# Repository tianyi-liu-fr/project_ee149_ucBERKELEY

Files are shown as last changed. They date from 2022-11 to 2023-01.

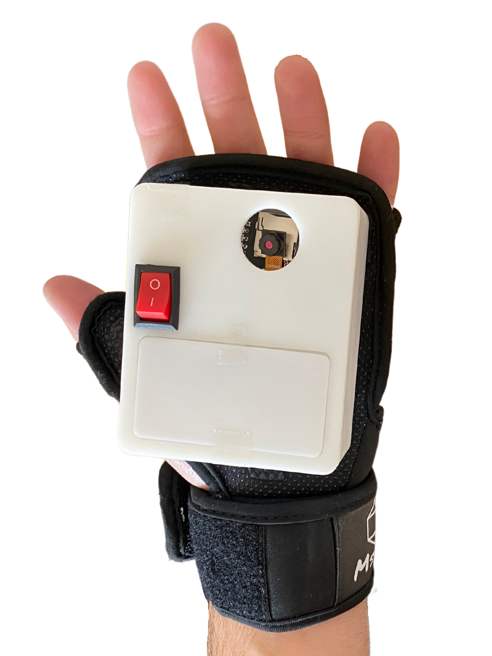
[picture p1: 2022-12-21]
Hardware/Device (front view).png

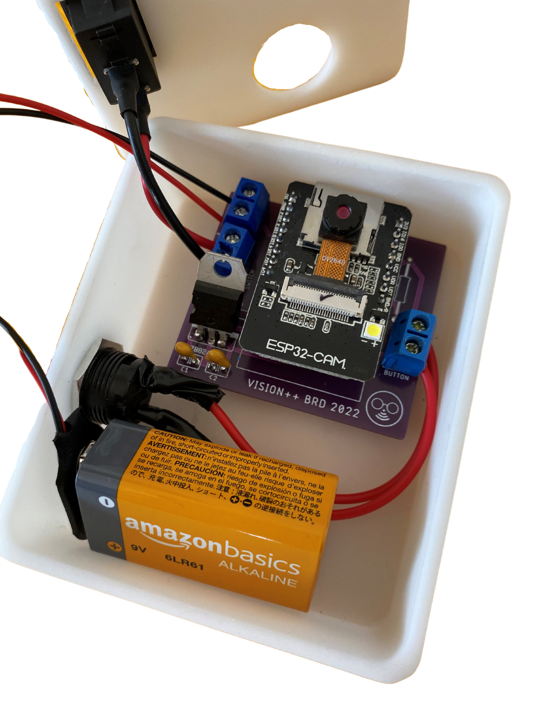
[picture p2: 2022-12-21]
Hardware/Open enclosure.png

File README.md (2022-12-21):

# EECS149/249 VISION++ Project
Project developed by Enrique Flores Medina and Tianyi Liu, as conceptualized by PhD Prabal Dutta.


Device and app

Vision++ is a glove designed to empower low vision people, by turning any readable text into speech. By pressing a button, the glove captures an image. If it contains any text, it is automatically turned into speech through a smartphone app. Demonstration video: https://youtu.be/q09WU-yeQec

# Hardware
The hardware folder contains the files used to design a PCB and an enclosure. The ESP32-CAM development board was used, and a PCB and enclosure were designed to adjust to its capabilities.

# Software
The software folder contains the source code for the ESP32-CAM, which allows it to capture and upload images to a cloud server with the press of a button. It also contains two python scripts: one downloads the images uploaded by the ESP32-CAM to the cloud server, and another one extracts the text detected in those images. Finally, the Smartphone App folder contains the file used to develop the app that turns the text into speech. Additionally, there is a Finite State Machine (FSM) diagram showing the behavior of each piece of software.

# Documentation
The documentation folder includes the project proposal and two milestones, showing how the project started, how it progressed, and how it turned out in the end.

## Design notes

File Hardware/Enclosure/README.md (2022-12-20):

# Enclosure CAD
Consists of 3 separate parts: A base, which contains the PCB, the battery, the power switch, and the button. A base cover, sealing everything inside the enclosure. A battery cover, which allows for battery replacement.

For the project, the enclosure was 3D printed with LEDO 6060 Resin, and the electronic components were attached to the enclosure with polymer glue.

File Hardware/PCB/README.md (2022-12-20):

# What is in the PCB?
The PCB allows for the connection of pin 13 in the ESP32-CAM board to GND through a push button, which serves as the trigger to capture images. It also allows for the use of power supplies from 5VDC up to 35VDC, by using an L7805 5V voltage regulator and two capacitors for noise filtering. Finally, the PCB is equipped with a voltage divisor that is connected to an ADC pin in the board. If a 9VDC battery is used as the power supply, two 10kOhm resistors can be used to measure its voltage level. This last part, however, is not yet implemented in the source code. 

The images show a CAD of the PCB and of the real assembled PCB. The real assembled PCB shown in outdated.

# Libraries
Footprint for the ESP32-CAM development board as ESP32-CAM.lbr, and footprint for the L7805 voltage regulator as L7805.lbr

# Board, Schematic, and Gerbers
Files for the PCB design are shown as PCB.brd, PCB.sch, and Gerbers.zip. The pinout for the ESP32-CAM development board can be found in: https://randomnerdtutorials.com/esp32-cam-ai-thinker-pinout/

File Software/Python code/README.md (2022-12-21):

# Python code
Two python scripts were used for the project.
1. Download images from Google Drive

This script automatically downloads the images taken by the camera and uploaded to the Google Drive folder. After they are downloaded, the script deletes them from Google Drive, minimizing the storage use of the cloud service.

2. AWS Textract

This script automatically processes the images downloaded to the computer by the previous script with AWS textract. After the text is detected, it is written in a Google Spreadsheet.

Note: Both python scripts are run simultaneously when the device is being used.

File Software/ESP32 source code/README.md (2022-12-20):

# Code to capture and upload images to Google Drive
A template source code to upload images to Google Drive using the ESP32-CAM board, found in the folder ESP32_GoogleDrive, was extracted from https://www.electroniclinic.com/esp32-cam-send-images-to-google-drive-iot-security-camera/. Copyright (c) 2022 Engr Fahad.

Three external libraries are used in the source code:
1. "esp_camera.h", which is the ESP32 camera driver. Copyright (c) 2015-2016 Espressif Systems (Shanghai) PTE LTD. License: https://github.com/espressif/esp32-camera
2. "Base64.h", used to encode binary into base64 strings. Copyright (c) 2013 Adam Rudd. License: https://github.com/adamvr/arduino-base64 
3. "soc.h", used to disable the brownout detector, which creates restrictions due to low power supply. Copyright (c) 2010-2022 SPDX-FileCopyrightText Espressif Systems (Shanghai) CO LTD. License: https://github.com/espressif/esp-idf/blob/master/components/soc/esp32/include/soc/soc.h

Furthermore, Arduino core for ESP32 was installed in the Arduino IDE, from https://github.com/espressif/arduino-esp32. The following URL https://raw.githubusercontent.com/espressif/arduino-esp32/gh-pages/package_esp32_index.json was added as a board manager to do so. Copyright (C) 1991, 1999 Free Software Foundation, Inc.

# Modifications to the original code
The original template source code sends a notification when the image is uploaded using Line Notify. This part was removed, since it was not necessary for the purposes of the project. Comments on the relevance of each line of code were added. The original code sends an image to Google Drive periodically using a delay in the main loop function. A GPIO pin set as an input was added to use a button as the trigger to send images. Furthermore, the number of frames that can be stored in the camera's buffer was reduced from 2 to 1, preventing the uploading of images that were not sent in previous triggerings of the button.

# Google Apps Script
A javascript Google Apps Script, which helps to provide credential authentication and upload images to specific Google Drive folders, was deployed. The deployment ID is used in the source code for the ESP32-CAM board. The template for the Google Apps Script was also extracted from https://www.electroniclinic.com/esp32-cam-send-images-to-google-drive-iot-security-camera/. Copyright (c) 2022 Engr Fahad. The notification with Line Notify was eliminated from the script.

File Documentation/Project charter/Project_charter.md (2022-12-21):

# VISION++
Team: Enrique Flores Medina, Tianyi Liu.

EECS 149/249A Project Charter, Fall, 2022

# Project Goal
This project will develop a glove that enables blind people to read, by turning (almost) any text they
encounter into speech.

# Project Approach
The project will convert any text into speech as described by a deterministic state machine that receives
multiple sensor inputs. One of these inputs will trigger a camera, which will take a picture and send it to a
computer. Then, the computer will read the text in the received image, and convert it into speech that can
be heard with either headphones or a speaker.

# Resources
Our plan is to use a microcontroller (SparkFun ESP32 Thing - DEV-13907) as the main distributor
between the embedded camera and the computer. The picture taken by the embedded camera will be
transferred wirelessly with BLE or WIFI. Then, using MATLAB’s OCR function, the text will be
extracted from the picture. Finally, the text will be turned into speech using MATLAB’s audio toolbox.
With regards to the embedded camera that will be used for the project, the first option would be the
ESP32-CAM WiFi Bluetooth Camera Module Development Board With Camera (D111), since it is the
most hardware friendly for the ESP32 board.

The first goal is the transferring of images from the microcontroller via WIFI/BLE. By pushing a button
(from the hardware inventory), the microcontroller should instruct the camera to take a picture, and send
it. The second goal is to use MATLAB to read and speak out all the text from the picture (from the
hardware inventory). Finally, the third goal would be the addition of an ultrasonic sensor (from the
hardware inventory) to instruct the user on a proper distance to take the picture from, but this is not the
main focus. The state machine would take, then, the ultrasonic sensor measurements and the button as
inputs.

# Schedule
● October 21: Project Proposal (this document) and creation of Github repository

● October 31: Architecture drawing (state machine), finalize the hardware list with GSI approval

● November 6: Milestone 1

● November 14: Reliable MATLAB script to read text from images taken with the embedded
camera and turn it into speech. Add a light source to illuminate the text every time the photo is
taken. Decide on the protocol to send the picture from the ESP32 to the computer.

● November 21: Midterm 2

● November 22: Prepare Milestone 2 and code to send the image from the microcontroller to the
computer.

● November 23: Milestone 2

● November 28 - December 2: Milestone 2 Meetings

● December 7: Finalize details, if there is extra time:
  1. Add ultrasonic sensor measurements to determine how far the user has to be from the text
to take the image properly.
  2. Create an app to hear the speech on the phone

● December 15: Project Poster/Demo Expo

● December 16: Peer Evaluations, Project report

# Risk and Feasibility
There are many unknowns. First, by sending the image from the microcontroller to the computer, some
packets could be lost. Therefore, the image could lose quality which would significantly reduce our ability
to detect the text in it. To deal with this, a comparison between the reliability of the image transmission
between BLE and serial bus could be taken. Another potential issue could be the latency from the trigger
of the camera to the speech, which could make the functionality of the product inefficient. If the system
consumes a lot of power, and the hardware components are not ergonomic for the user, the experience
would also be worsened.

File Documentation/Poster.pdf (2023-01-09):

# EECS 149/249A

Fall 2018 | VISION++

Enrique Flores Medina, Tianyi Liu

## Goals

VISION++ seeks to empower low vision people by providing them a glove that can turn any text into speech.

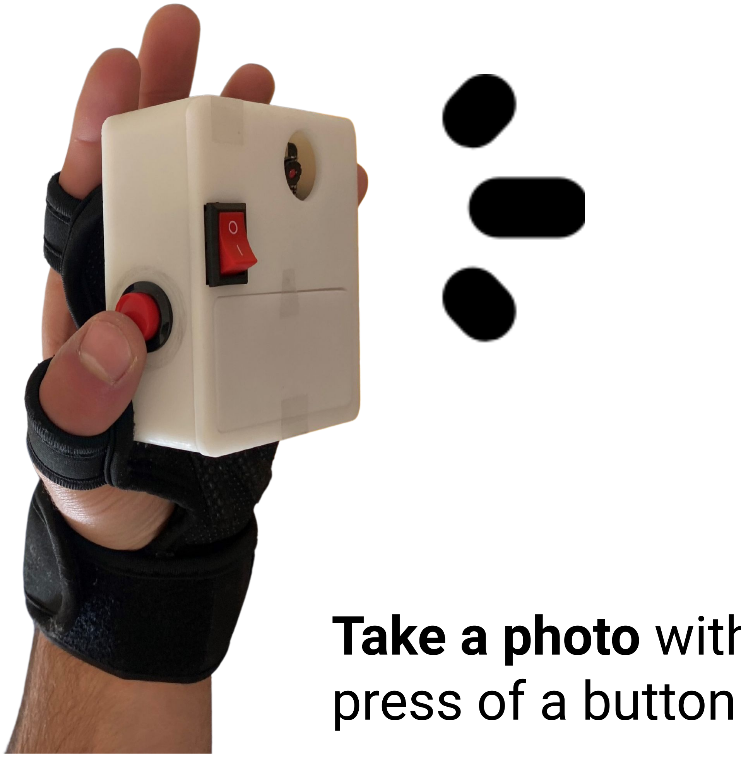
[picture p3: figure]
press of a button
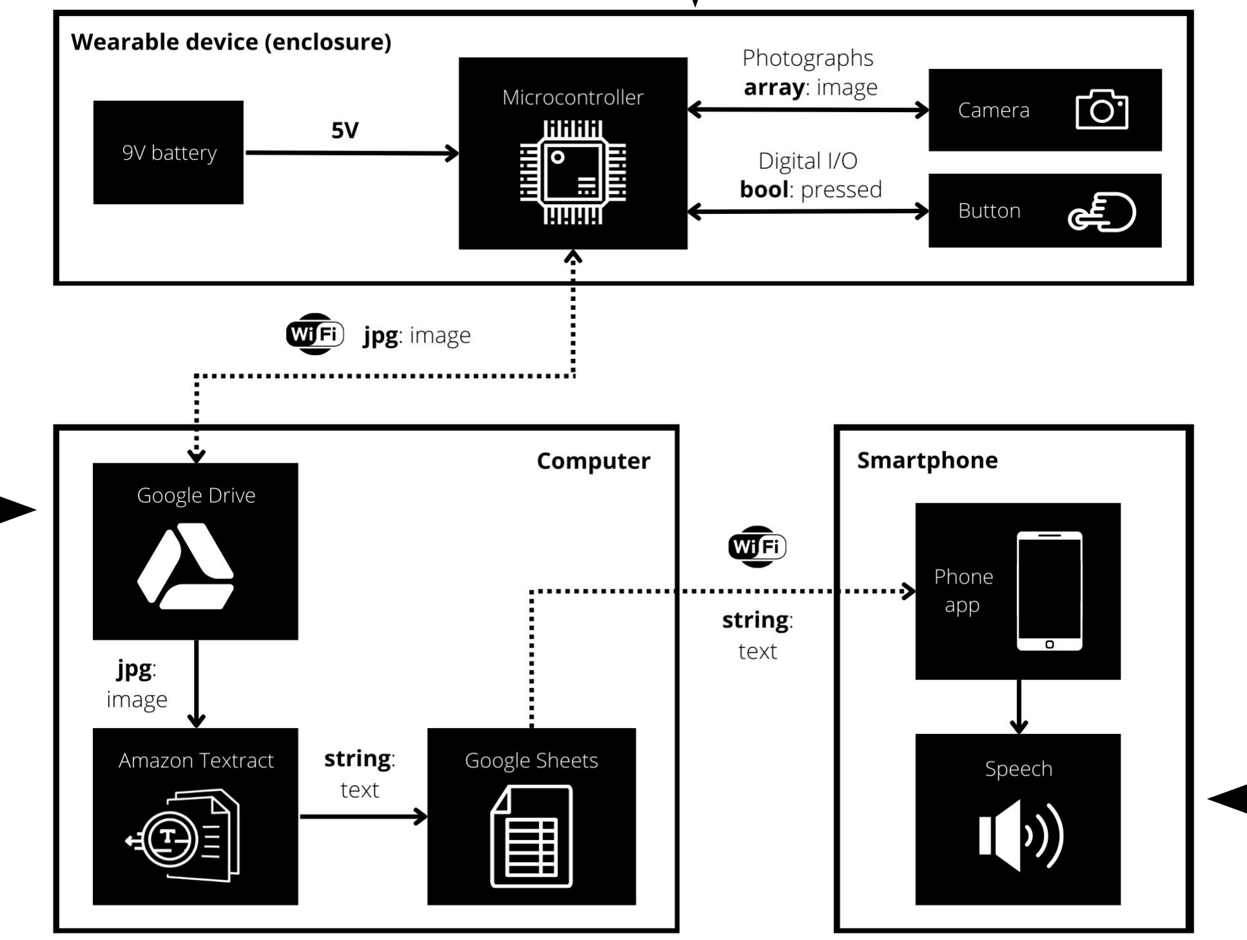
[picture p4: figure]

Take a photo with the

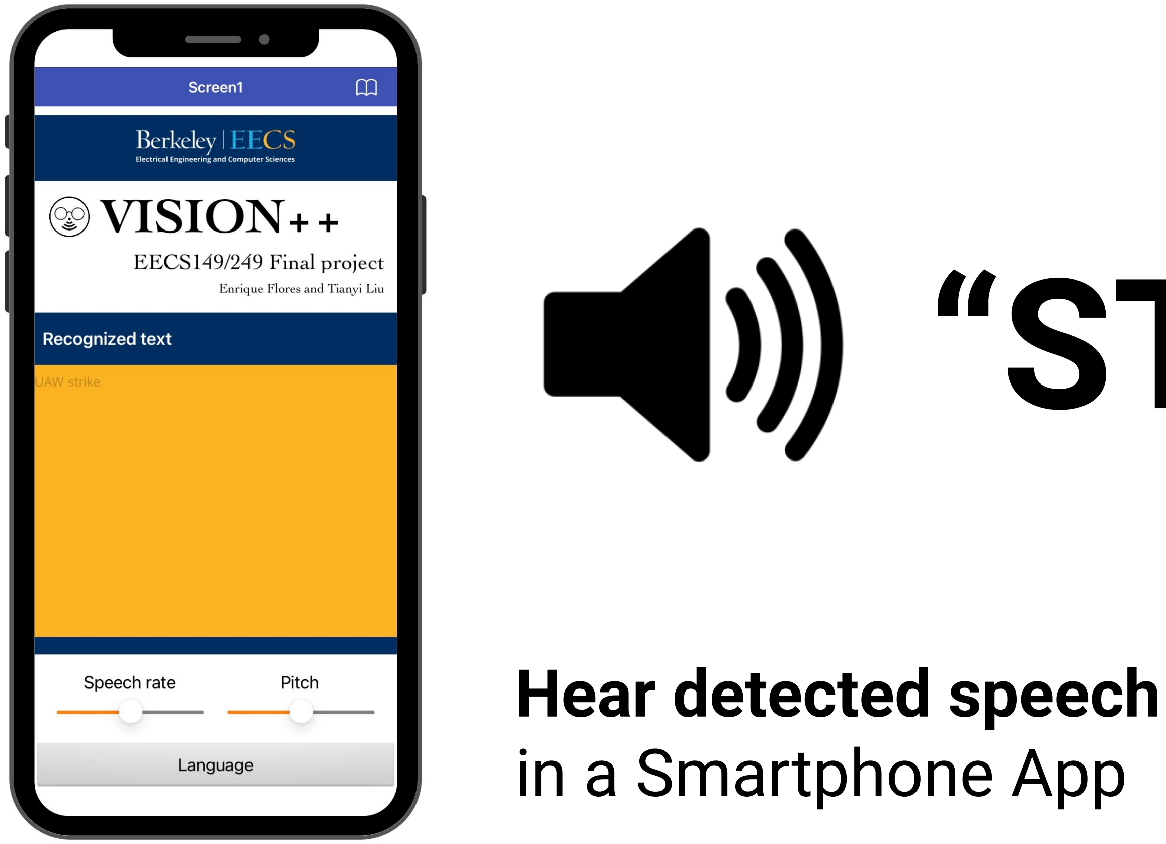
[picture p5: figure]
Hear detected speech in a Smartphone App

The glove includes an
ESP32-CAM development board, which includes a wifi module, an OV2640 camera, an easy to

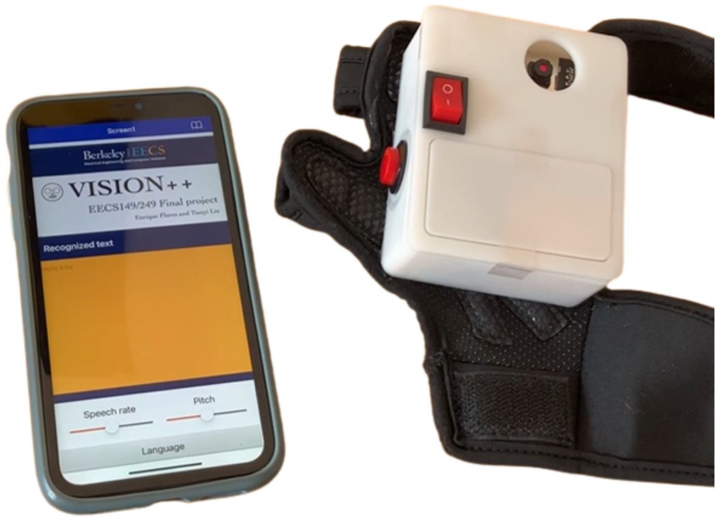
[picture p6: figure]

replace 9V battery, and a button. The app allows the user to select a language, speech rate and pitch.

### 1. Enable your phone’s

hotspot.

### 2. Turn on device and

wait for it to connect
to the network.

### 3. Ready to use!

## Project architecture

The following diagram shows the communication between the different parts that make up the project.

This is in the glove

## Behavior of the system

2022

# “STOP”

## What is in the glove and app?

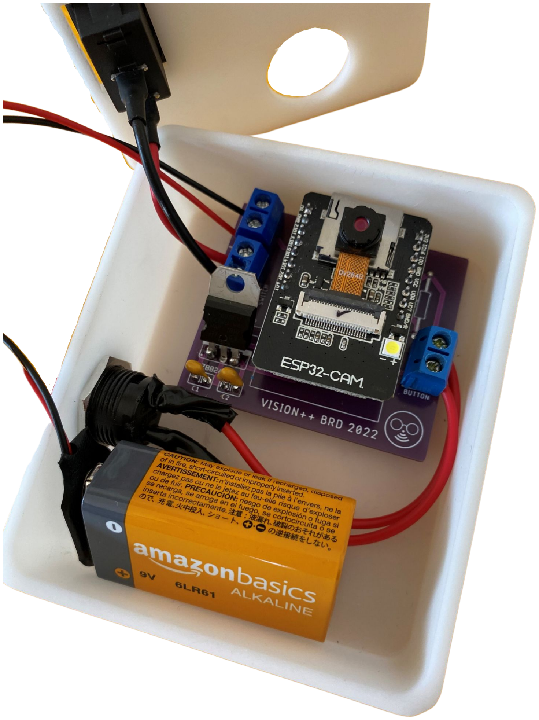
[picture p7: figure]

## How can I use it?

Now, press the button
and hear the speech

A computer

Smartphone

- The glove captures an image and uploads it to Google Drive through WiFi
- A computer downloads it, extracts the text with AWS Textract, and uploads it to a Google Spreadsheet
- The smartphone app turns the text into speech

The following state
machine displays the
behavior of the entire
system.

The only input is the push of the button, and the speaker

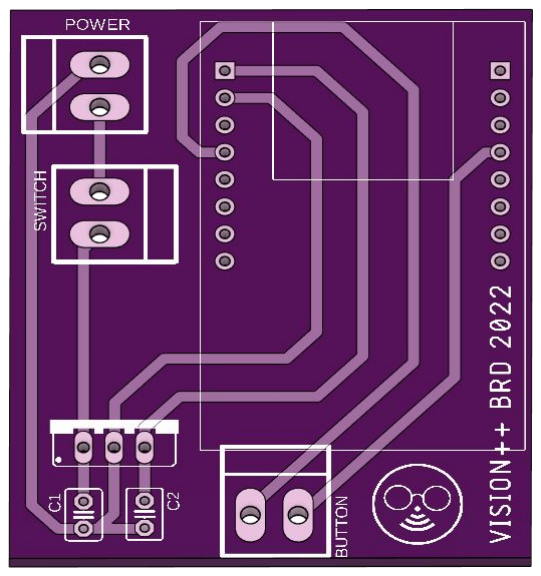
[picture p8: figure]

of the phone and the
camera of the glove are
treated as outputs

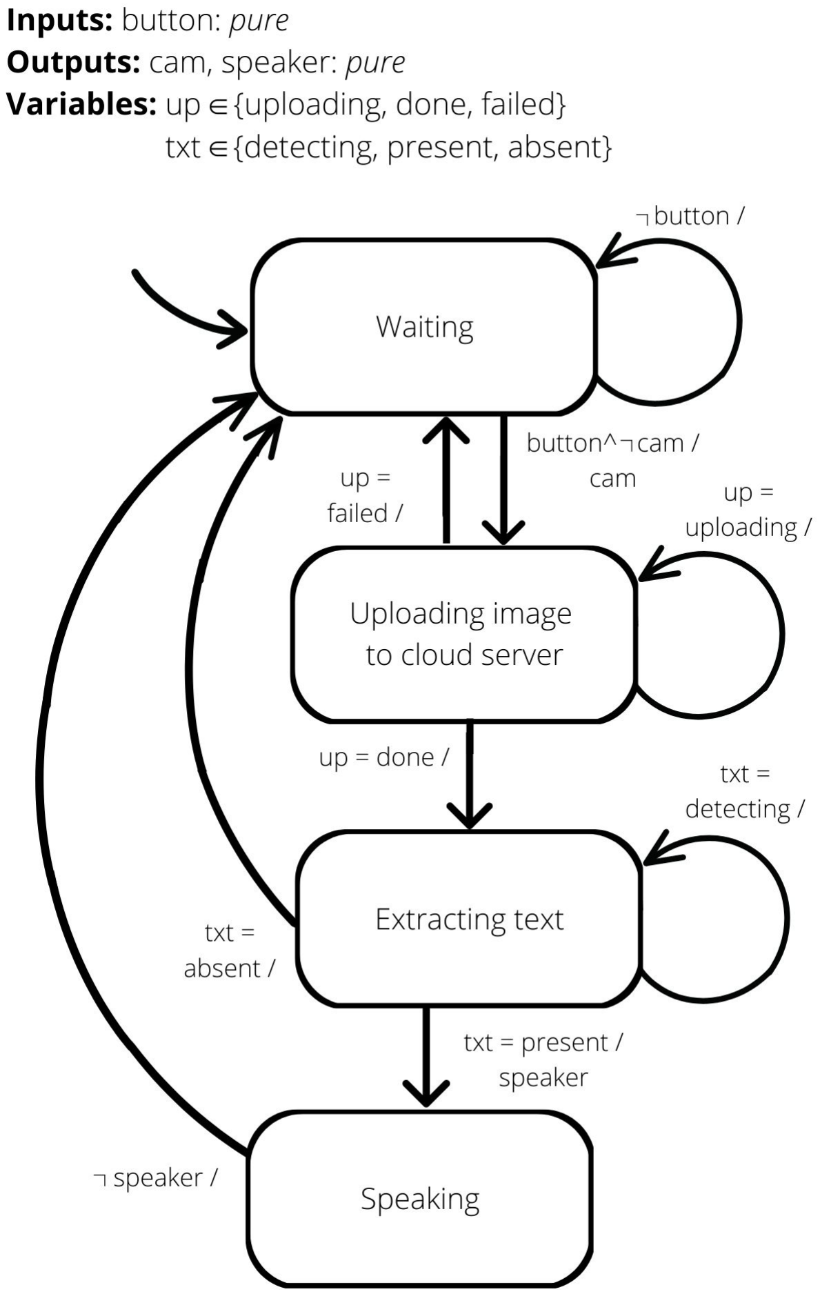
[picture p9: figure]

## Customized PCB

A custom PCB was
designed to minimize
the physical use of
space in the glove. It
connects a voltage
regulator to the
ESP32-CAM board, and
drives a GPIO pin to
GND when a button is
pressed

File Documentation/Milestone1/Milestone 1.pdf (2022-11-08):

### Project Title: Vision++ Team: Enrique Flores Medina, Tianyi Liu EECS 149/249A Project Charter, Fall, 2022

### Architecture drawing:

The following architecture drawing shows the complete scheme and reach of our project. The connections made with solid lines are wired connections, while the dotted lines are wireless network connections. In bold letters are shown the data types for all the transmitted information.

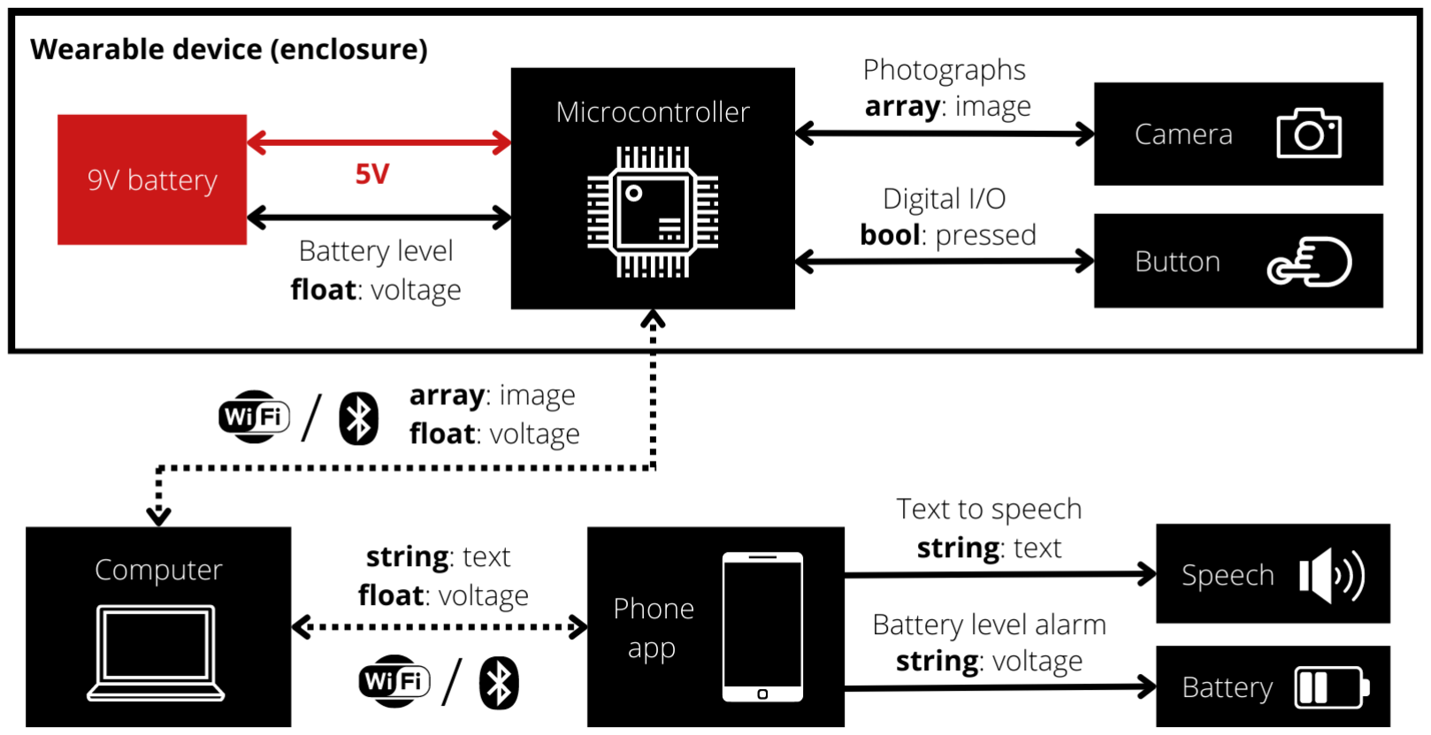
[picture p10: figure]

Figure 1. Architecture drawing of the project

### Progress so far:

Made an initial sketch of the wearable device. This helped us obtain a general overview on how to make the design ergonomic and the dimension limits we will be working with. The sketch is shown in figure 2.

A first draft for the PCB design that will be contained in the enclosure of the wearable device was also made. This includes all the parts that are inside the wearable device rectangle in the architecture drawing of figure 1. The CAD design, as well as the schematic for the circuit, are shown in figure 3.

Also drew the state machine that models the behavior of our system. It can be found in the GitHub repository.

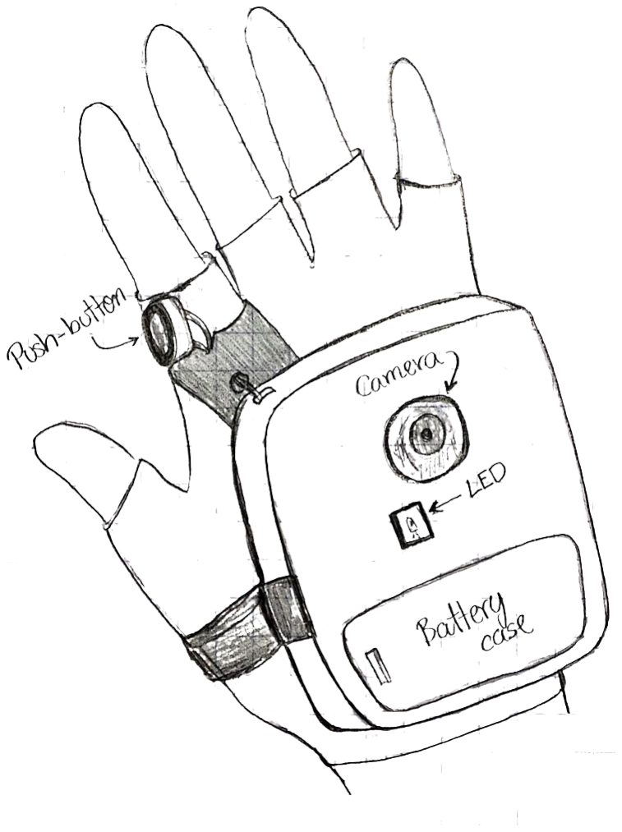
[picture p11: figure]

Figure 2. Initial sketch of wearable device.

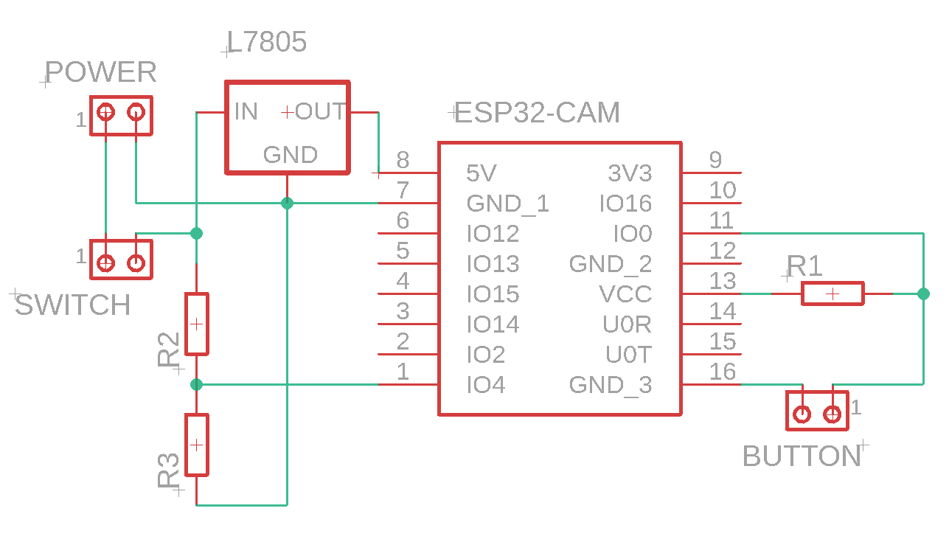
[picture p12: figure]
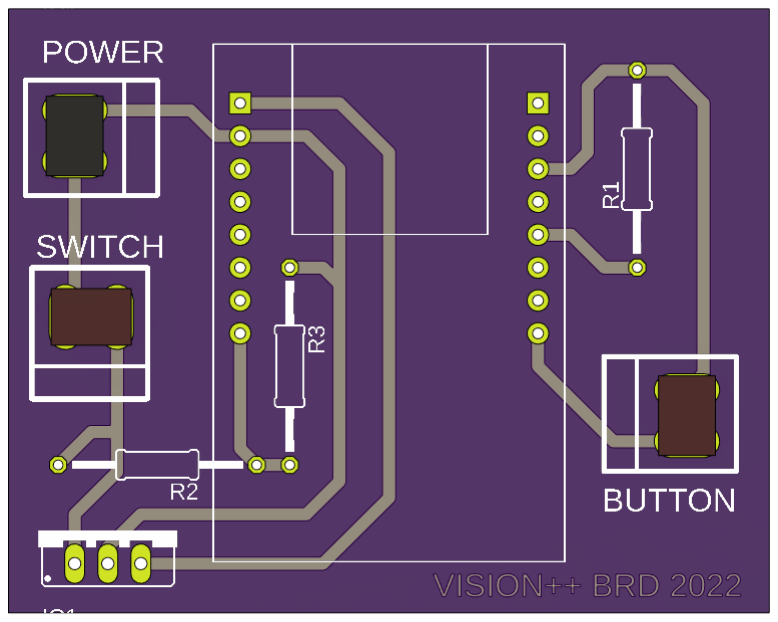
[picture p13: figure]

Figure 3. CAD and PCB schematic for the wearable device.

We started testing with MATLAB to read the text using the OCR function. More work is needed to process the text and turn it into a string that is easy to read, but we now have the initial code to read text from images, and to also turn it into speech using a third party connected to MATLAB. To add to this, we started developing an app that will turn the text from the images into speech. (All the figures and files for this section are on GitHub).

Finally, we purchased and requested all the necessary components for the project. The full list is shown in resources.

### Goals:

Our goal is still to turn any text into speech, however, our deterministic state machine now only receives one sensor input, which is the button signal. This button will instruct the camera to take a picture, and send it to a computer. Then, the computer will read the text in the received image, and, instead of turning it into speech right there, it will send it to a smartphone app. Finally, the app will convert the aforementioned text into speech that can be heard with either headphones or a speaker.

### Resources:

We will use the following libraries for our ESP32 development board, using an arduino IDE:

1. To build a web server and upload the images:
a. https://github.com/me-no-dev/ESPAsyncWebServer
b. https://github.com/me-no-dev/AsyncTCP
2. To take, process, and send the images through wifi
a. WiFi.h, Esp_camera.h, Esp_timer.h, and Img_converters.h

The pinout reference for the ESP32 chip, which the ESP32-CAM development board uses: https://randomnerdtutorials.com/esp32-pinout-reference-gpios/

The MATLAB OCR function is part of MATLAB’s pre installed libraries, and our smartphone app will be developed using App Inventor:

https://appinventor.mit.edu/

The parts and mechanical assembly tools we need:

1. 9V battery, and clip (https://www.amazon.com/-/es/dp/B01IFP0N3U?psc=1&ref=ppx_yo2ov_dt_b_product_details)
2. L7805CV Voltage regulator 5V (https://docs.google.com/spreadsheets/d/1xp9HDOxKFIU9-VqwIetH1_nhR8PGKd3AOYcG0yj5ntE/edit#gid=0)
3. ESP32-CAM development board with FTDI programmer (https://vetco.net/products/esp32-cam-wifi-bluetooth-camera-module-development-board-with-camera-d111/vupn998)
4. Momentary push button (https://www.electromaker.io/shop/product/panel-mount-red-momentary-pushbutton)
5. Male and female pin headers (https://www.electromaker.io/search?query=headers)
6. Three 1kΩ resistors
7. Three 5mm 2 pin screw terminals (https://www.electromaker.io/shop/product/screw-terminals-5mm-pitch-2-pin)
8. Blank PCB board (at least 60mm x 50 mm)
9. Polymer glue (to attach the PCB to the enclosure)
10. Velcro tape
11. 3D printer
12. PCB printer
13. Gym or exercise glove

### Updated schedule:

- November 6: Milestone 1 - Present architecture drawing, conceptual sketch, and PCB design for the wearable device.
- November 14: Reliable MATLAB script to read text from images taken with the embedded camera. Code to send images from the ESP32 to a web server. Print the PCB and finalize the enclosure CAD.
- November 21: Midterm 2, 3D print enclosure.
- November 22: Code to run MATLAB script when an image is uploaded to the web server, and retrieve said image. Finalize design of smartphone app.
- November 23: Milestone 2 - Showcase progress until this point.
- November 28 - December 2: Milestone 2 Meetings
- December 7: Smartphone app to read the text files that the MATLAB script outputs, and turn it into speech. Finalize details on the rest of the project.
- December 15: Project Poster/Demo Expo
- December 16: Peer Evaluations, Project report

### Risk and Feasibility

There are many unknowns. First, by sending the image from the microcontroller to the computer, some packets could be lost. Therefore, the image could lose quality which would significantly reduce our ability to detect the text in it. Another potential issue could be the latency from the trigger of the camera to the speech, which could make the functionality of the product inefficient. If the system consumes a lot of power, and the hardware components are not ergonomic for the user, the experience would also be worsened. The quality of the ESP32-CAM camera is a big factor in determining if we can reliably read the text or not. Finally, the time that the hardware takes to arrive is also important, since it determines how much work can be done.

### Link to GitHub:

https://github.com/tianyi-liu-fr/project_ee149_ucBERKELEY

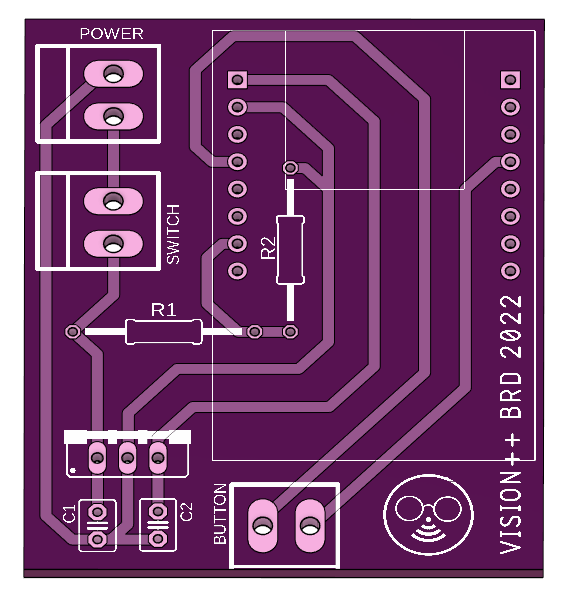
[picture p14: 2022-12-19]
Hardware/PCB/PCB.png

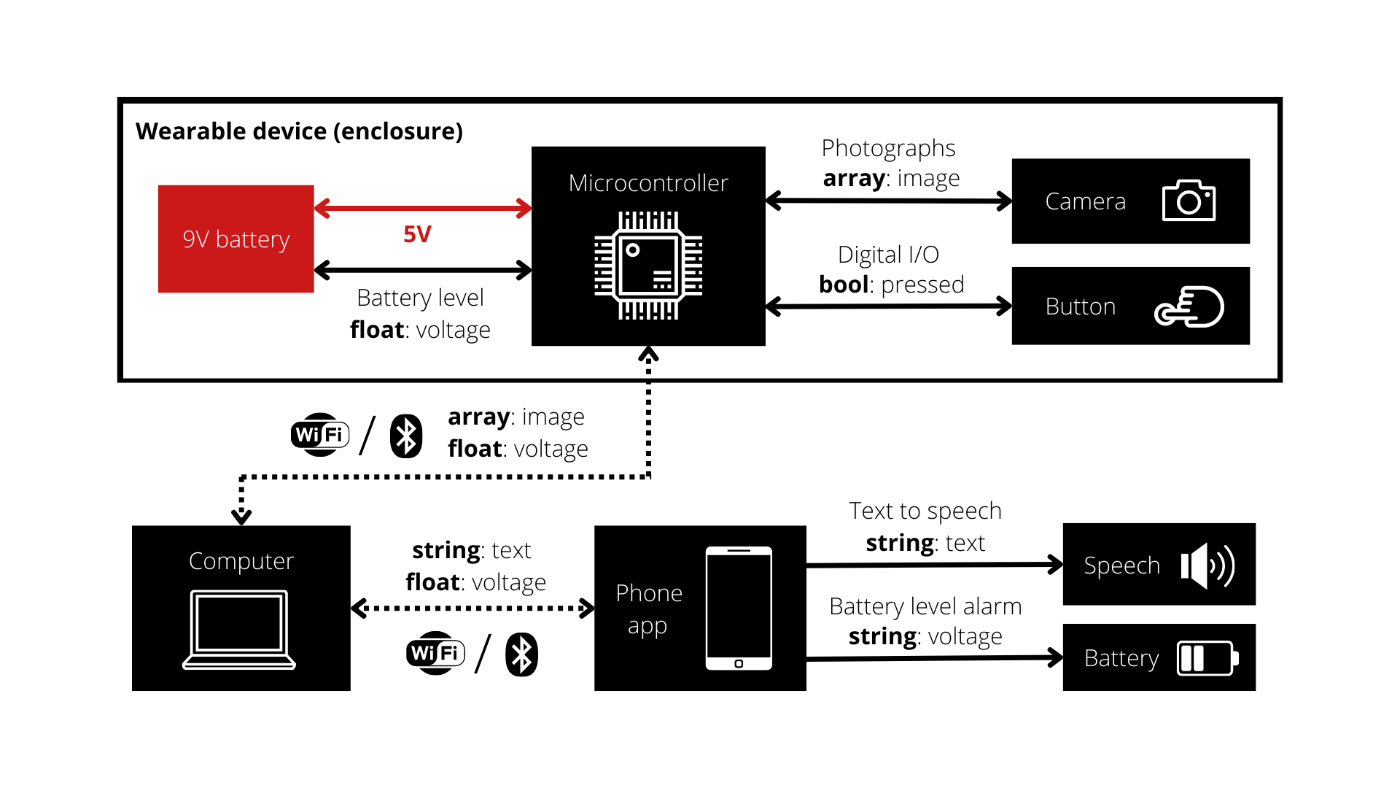
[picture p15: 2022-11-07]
Documentation/Milestone1/Architecture drawing.png

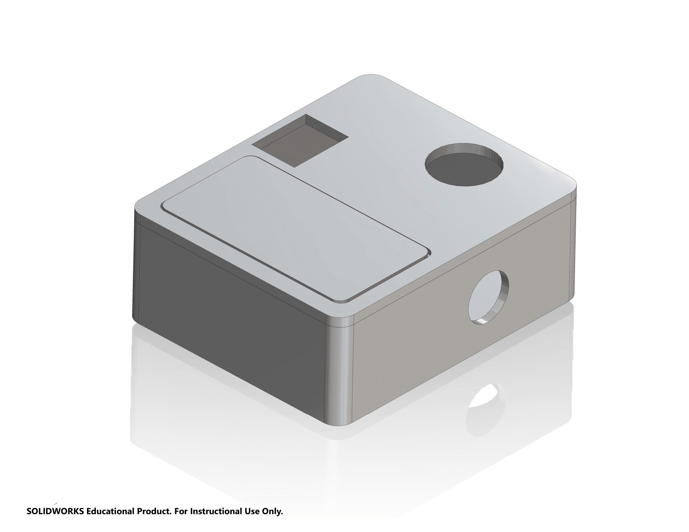
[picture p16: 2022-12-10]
Hardware/Enclosure/Enclosure.png

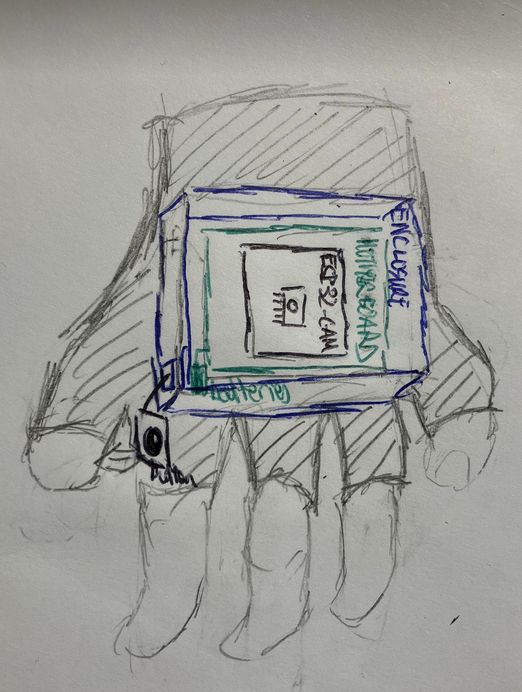
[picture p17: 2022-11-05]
Documentation/Milestone1/Conceptual sketch 3.png

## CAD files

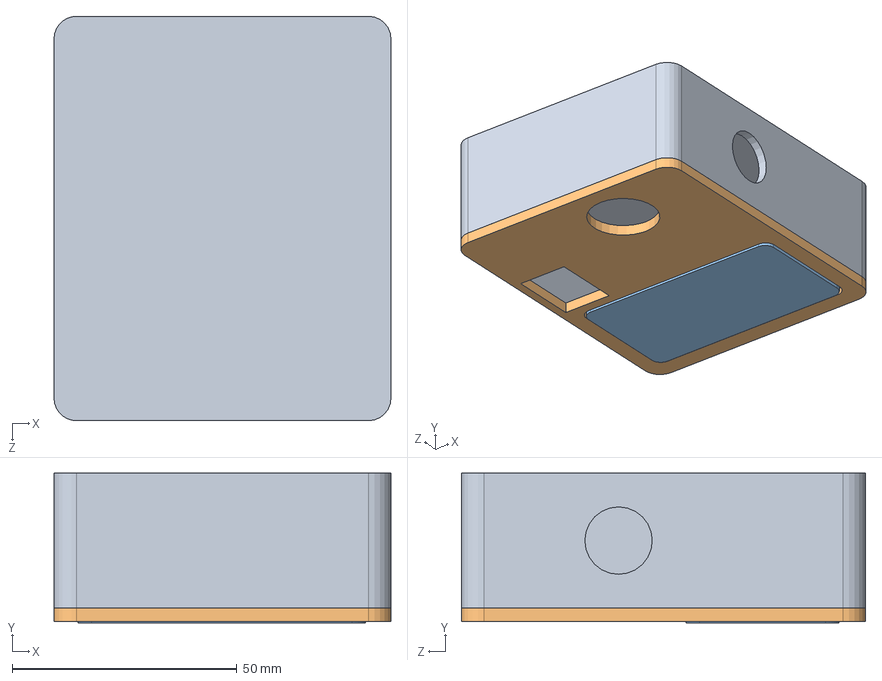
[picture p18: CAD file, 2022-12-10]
Hardware/Enclosure/Enclosure.SLDASM
75.0 x 33.3 x 90.0 mm
Base
Cover
Battery cover

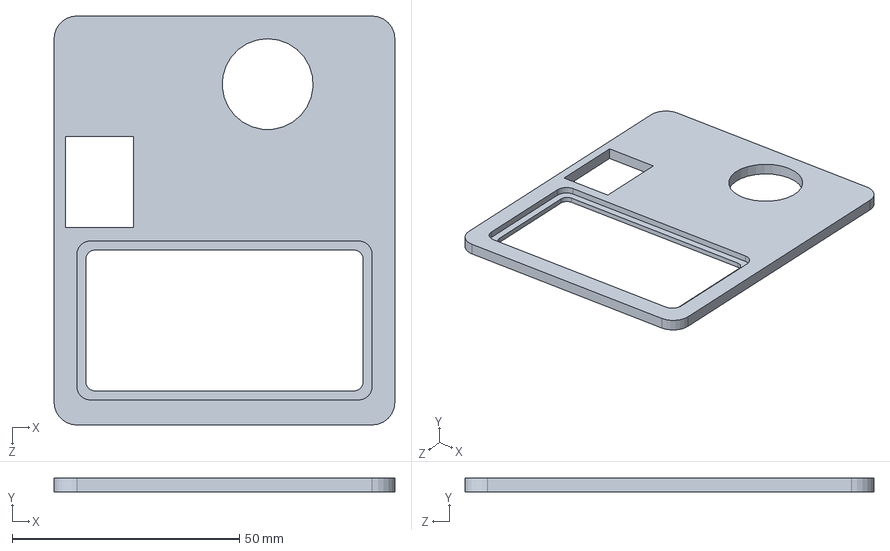
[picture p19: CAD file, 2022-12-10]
Hardware/Enclosure/Cover.SLDPRT
75.0 x 3.00 x 90.0 mm

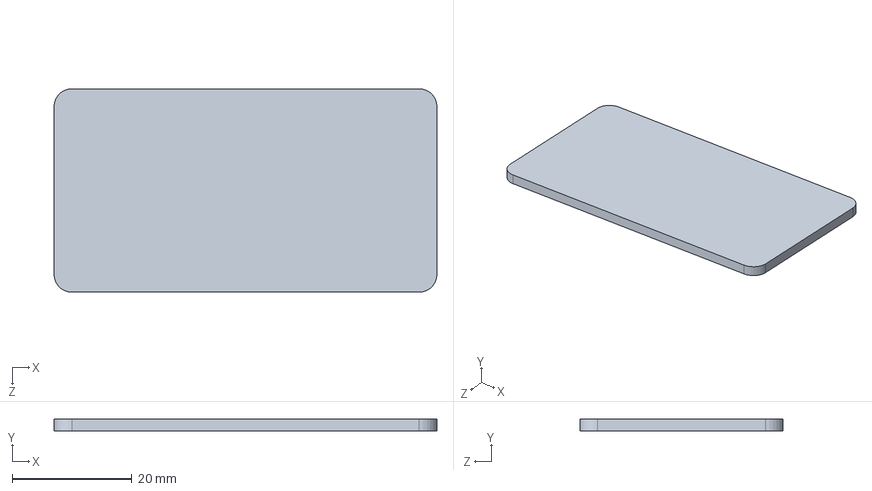
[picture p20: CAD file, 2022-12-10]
Hardware/Enclosure/Battery cover.SLDPRT
64.0 x 2.00 x 34.0 mm

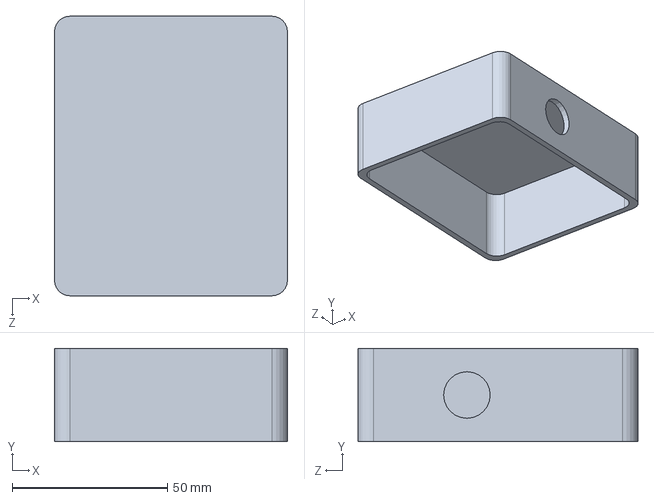
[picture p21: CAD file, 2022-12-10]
Hardware/Enclosure/Base.SLDPRT
75.0 x 30.0 x 90.0 mm

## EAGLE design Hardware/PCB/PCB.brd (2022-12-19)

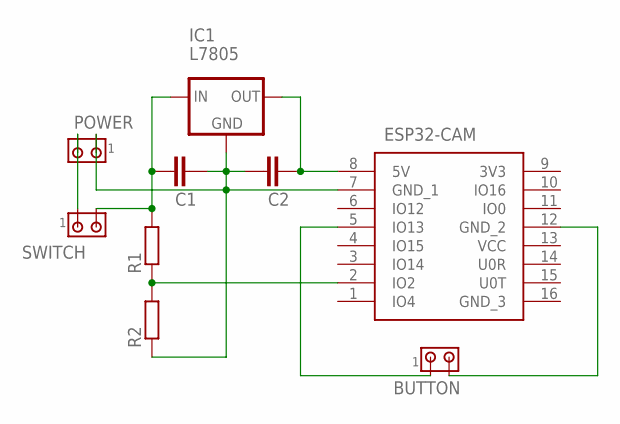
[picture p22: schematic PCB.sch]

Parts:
BUTTON: MTA02-156; 1X2MTA
C1, C2: C2,5-3; C2.5-3
IC1: L7805; 78XXS
POWER: MTA02-156; 1X2MTA
R1, R2: R-EU_0207/15; 0207/15
SWITCH: MTA02-156; 1X2MTA
U$1: ESP32-CAM

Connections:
unnamed: BUTTON.2, U$1.12 (GND_2)
unnamed: BUTTON.1, U$1.5 (IO13)
unnamed: POWER.2, SWITCH.1
unnamed: C1.2, C2.1, IC1.GND, POWER.1, R2.1, U$1.7 (GND_1)
unnamed: C2.2, IC1.OUT, U$1.8 (5V)
unnamed: C1.1, IC1.IN, R1.2, SWITCH.2
unnamed: R1.1, R2.2, U$1.2 (IO2)

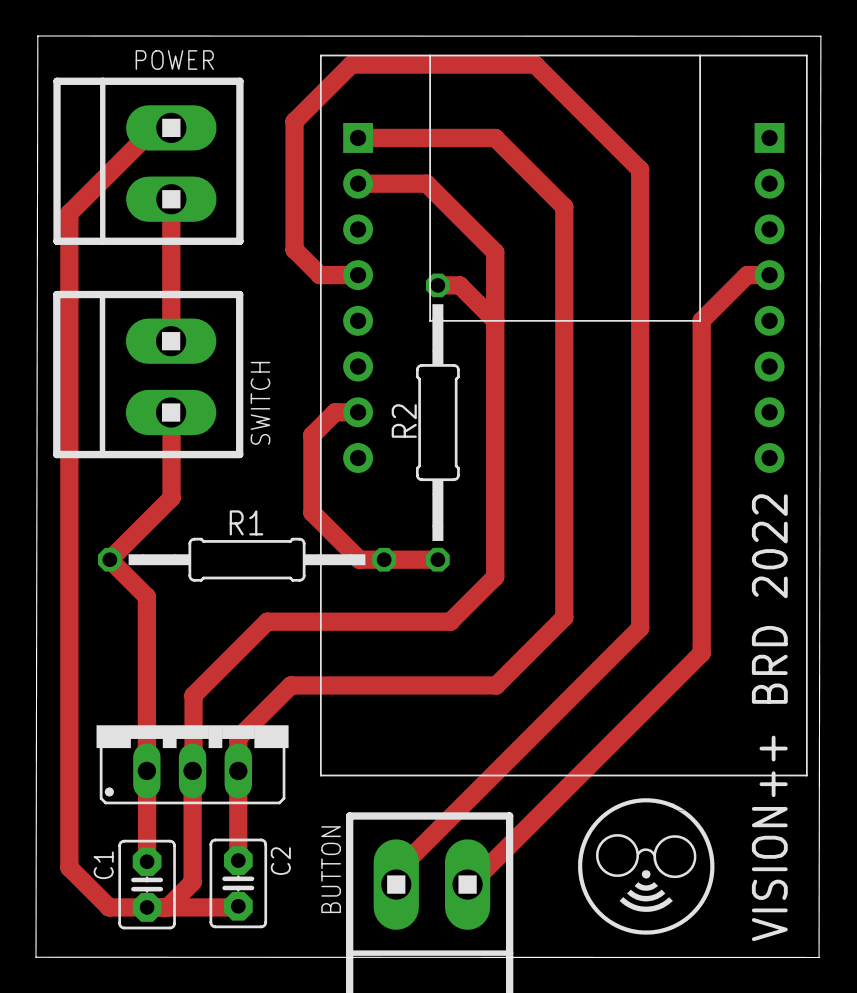
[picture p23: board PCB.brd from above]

Board: 2 copper layers, 43.6 x 51.2 mm, 9 parts (0 on the bottom side), 7 nets.

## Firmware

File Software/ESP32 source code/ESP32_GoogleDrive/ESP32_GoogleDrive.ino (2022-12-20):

// Wifi libraries
#include <WiFi.h>
#include <WiFiClientSecure.h>
// Header to disable brownout detector (restrictions due to low power supply). SPDX-FileCopyrightText: 2010-2022 Espressif Systems (Shanghai) CO LTD. License: https://github.com/espressif/esp-idf/blob/master/components/soc/esp32/include/soc/soc.h 
#include "soc/soc.h"
#include "soc/rtc_cntl_reg.h"
// Header to encode binary into base64 strings. Copyright (c) 2013 Adam Rudd. License: https://github.com/adamvr/arduino-base64 
#include "Base64.h"
// Header for ESP32 camera driver. Copyright (c) 2015-2016 Espressif Systems (Shanghai) PTE LTD. License: https://github.com/espressif/esp32-camera 
#include "esp_camera.h"

// Phone's wifi connection
const char* ssid     = "Enrique's iPhone";   // Network SSID
const char* password = "12345678";           // Network password

// Button pins and initial state of button
int button = 13;
int state = LOW;

// Link to Google Apps Script that uploads the image taken to Google Drive
String myScript = "/macros/s/AKfycbxXYiwpzA570zGmZNNPbPZcG9V3fTSWX42qMTpsU6ZHQJ7r4cylNIBdsOFfoQG_rEws/exec";
// Name of folder to save the images taken
String myFoldername = "&myFoldername=Visionplusplus photos";
// The image's file name
String myFilename = "&myFilename=vision_photo.jpg";
// Variable to store the image URL
String myImage = "&myFile=";

// CAMERA_MODEL_AI_THINKER pins. 
// ESP32 board with PSRAM is required to use these pins, such as the ESP32 Wrover Module.
#define PWDN_GPIO_NUM     32
#define RESET_GPIO_NUM    -1
#define XCLK_GPIO_NUM      0
#define SIOD_GPIO_NUM     26
#define SIOC_GPIO_NUM     27

#define Y9_GPIO_NUM       35
#define Y8_GPIO_NUM       34
#define Y7_GPIO_NUM       39
#define Y6_GPIO_NUM       36
#define Y5_GPIO_NUM       21
#define Y4_GPIO_NUM       19
#define Y3_GPIO_NUM       18
#define Y2_GPIO_NUM        5
#define VSYNC_GPIO_NUM    25
#define HREF_GPIO_NUM     23
#define PCLK_GPIO_NUM     22

void setup()
{
  // Set GPIO pin for button as input
  pinMode(button, INPUT);
  // Disable brownout detector to 
  WRITE_PERI_REG(RTC_CNTL_BROWN_OUT_REG, 0);
  
  Serial.begin(115200);
  delay(10);
  
  WiFi.mode(WIFI_STA);

  // Start trying to establish connection to selected wifi network
  Serial.println("");
  Serial.print("Connecting to ");
  Serial.println(ssid);
  WiFi.begin(ssid, password);  
  
  // Attempt to connect to wifi for 10 seconds
  long int StartTime=millis();
  while (WiFi.status() != WL_CONNECTED) 
  {
    delay(500);
    if ((StartTime+10000) < millis()) break;
  } 

  Serial.println("");
  Serial.println("STAIP address: ");
  Serial.println(WiFi.localIP());
    
  Serial.println("");

  // Blink led once if the connection failed
  if (WiFi.status() != WL_CONNECTED) {
    Serial.println("Reset");
    
    ledcAttachPin(4, 3);
    ledcSetup(3, 5000, 8);
    ledcWrite(3,10);
    delay(200);
    ledcWrite(3,0);
    delay(200);    
    ledcDetachPin(3);
  
    // Restart and retry to connect
    delay(1000);
    ESP.restart();
  }
  else {
  // Blink led five times if the connection succeeded
    ledcAttachPin(4, 3);
    ledcSetup(3, 5000, 8);
    for (int i=0;i<5;i++) {
      ledcWrite(3,10);
      delay(200);
      ledcWrite(3,0);
      delay(200);    
    }
    ledcDetachPin(3);      
  }

  // Configure all the ESP32 chip pins that correspond to the camera and led
  camera_config_t config;
  config.ledc_channel = LEDC_CHANNEL_0;
  config.ledc_timer = LEDC_TIMER_0;
  config.pin_d0 = Y2_GPIO_NUM;
  config.pin_d1 = Y3_GPIO_NUM;
  config.pin_d2 = Y4_GPIO_NUM;
  config.pin_d3 = Y5_GPIO_NUM;
  config.pin_d4 = Y6_GPIO_NUM;
  config.pin_d5 = Y7_GPIO_NUM;
  config.pin_d6 = Y8_GPIO_NUM;
  config.pin_d7 = Y9_GPIO_NUM;
  config.pin_xclk = XCLK_GPIO_NUM;
  config.pin_pclk = PCLK_GPIO_NUM;
  config.pin_vsync = VSYNC_GPIO_NUM;
  config.pin_href = HREF_GPIO_NUM;
  config.pin_sscb_sda = SIOD_GPIO_NUM;
  config.pin_sscb_scl = SIOC_GPIO_NUM;
  config.pin_pwdn = PWDN_GPIO_NUM;
  config.pin_reset = RESET_GPIO_NUM;
  config.xclk_freq_hz = 20000000;

  // Set format to JPEG
  config.pixel_format = PIXFORMAT_JPEG;

  // Initialize with high specs to pre-allocate larger buffers
  if(psramFound()){
    // Frame size for modules with PSRAM (1600 x 1200 px)
    config.frame_size = FRAMESIZE_UXGA;
    // Image quality from 0-63. Lower number means higher quality
    config.jpeg_quality = 6; 
    // Only allocate one image in the buffer
    config.fb_count = 1;
  } else {
    // Frame size for modules with PSRAM (800 x 600 px)
    config.frame_size = FRAMESIZE_SVGA;
    // Image quality from 0-63. Lower number means higher quality
    config.jpeg_quality = 6;
    // Only allocate one image in the buffer
    config.fb_count = 1;
  }
  
  // Initialize communication with camera
  esp_err_t err = esp_camera_init(&config);
  if (err != ESP_OK) {
    Serial.printf("Camera init failed with error 0x%x", err);
    delay(1000);
    ESP.restart();
  }

  // Drop down frame size for higher initial frame rate
  sensor_t * s = esp_camera_sensor_get();
  s->set_framesize(s, FRAMESIZE_VGA);  
}

void loop() {
  // Poll the button
  state = digitalRead(button);
    // If the button is pressed, capture and upload the image
    if (state == LOW){
      SendCapturedImage();
      delay(1000);
  }
}

String SendCapturedImage() {
  // Google Apps Script will be used to upload the image to Google Drive
  const char* myDomain = "script.google.com";
  String getAll="", getBody = "";

  // Counter of number of frames in the buffer
  int count = 0;
  
  // Set variable to store image
  camera_fb_t * fb = NULL;
  // Capture image
  fb = esp_camera_fb_get();  

  // Detect if the image was taken, by checking if it has any content
  if(!fb) {
    Serial.println("Camera capture failed");
    delay(1000);
    // Restart ESP32 if the camera did not capture the image
    ESP.restart();
    return "Camera capture failed";
  }  
  
  // Connect to Google Apps Script to upload captured image to Google Drive
  Serial.println("Connect to " + String(myDomain));
  WiFiClientSecure client_tcp;
  client_tcp.setInsecure();   
  
  // Check if the connection was succesful
  if (client_tcp.connect(myDomain, 443)) {
    Serial.println("Connection successful");

    // Set the format to jpeg for the images in the buffer
    while(count <= 2){
      char *input = (char *)fb->buf;
      char output[base64_enc_len(3)];
      String imageFile = "data:image/jpeg;base64,";
      for (int i=0;i<fb->len;i++) {
        base64_encode(output, (input++), 3);
        if (i%3==0) imageFile += urlencode(String(output));
      }

      // Input to Google Apps Script, specifying where to store the image in Google Drive
      String Data = myFoldername+myFilename+myImage;

      // Only upload the first image in the buffer, which is the first image taken
      if(count == 0) {
        client_tcp.println("POST " + myScript + " HTTP/1.1");
        client_tcp.println("Host: " + String(myDomain));
        client_tcp.println("Content-Length: " + String(Data.length()+imageFile.length()));
        client_tcp.println("Content-Type: application/x-www-form-urlencoded");
        client_tcp.println("Connection: keep-alive");
        client_tcp.println();
      }
      
      // Provide inputs to Google Apps Script
      client_tcp.print(Data);
      int Index;
      for (Index = 0; Index < imageFile.length(); Index = Index+1000) {
        client_tcp.print(imageFile.substring(Index, Index+1000));
      }

      // Increase counter
      count = count + 1;
      esp_camera_fb_return(fb);
    }
    
    // Define a 10 second timeout to upload the image
    int waitTime = 10000;   
    long startTime = millis();
    bool state = false;
    
    while ((startTime + waitTime) > millis())
    {
      // Print continuous ... in serial bus while the image is uploaded
      Serial.print(".");
      delay(100);      
      while (client_tcp.available()) 
      {
          char c = client_tcp.read();
          if (state==true) getBody += String(c);        
          if (c == '\n') 
          {
            if (getAll.length()==0) state=true; 
            getAll = "";
          } 
          else if (c != '\r')
            getAll += String(c);
          startTime = millis();
       }
       // Stop when the image is sent
       if (getBody.length()>0) break;
    }
    client_tcp.stop();
    Serial.println(getBody);
  }
  else {
    // Print in serial bus if the connection with the Google Apps Script fails or is timed out
    getBody="Connected to " + String(myDomain) + " failed.";
    Serial.println("Connected to " + String(myDomain) + " failed.");
  }
  
  return getBody;
}

// Function to encode the image URL
String urlencode(String str)
{
    String encodedString="";
    char c;
    char code0;
    char code1;
    char code2;
    for (int i =0; i < str.length(); i++){
      c=str.charAt(i);
      if (c == ' '){
        encodedString+= '+';
      } else if (isalnum(c)){
        encodedString+=c;
      } else{
        code1=(c & 0xf)+'0';
        if ((c & 0xf) >9){
            code1=(c & 0xf) - 10 + 'A';
        }
        c=(c>>4)&0xf;
        code0=c+'0';
        if (c > 9){
            code0=c - 10 + 'A';
        }
        code2='\0';
        encodedString+='%';
        encodedString+=code0;
        encodedString+=code1;
      }
      yield();
    }
    return encodedString;
}
